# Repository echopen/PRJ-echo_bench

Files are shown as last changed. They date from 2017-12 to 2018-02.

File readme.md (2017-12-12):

Project
=======

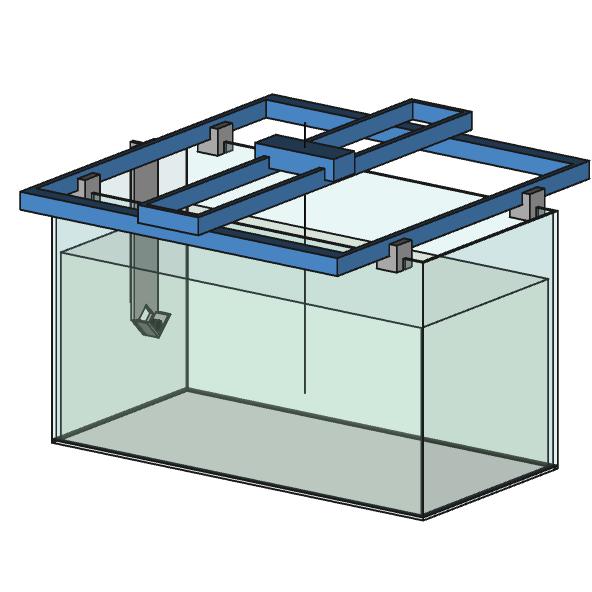
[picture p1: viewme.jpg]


Name
----

[2017-09-01 PRJ echo_bench]

Title
-----

Automatic ultrasonic transducers characterisation test bench

Description
-----------

This test bench is dedicated to the measurement of ultrasonic transducer
performances, such as:

-   experimental identification of the optical focus;

-   characterisation of the sound field in two dimensions (for example on a 5 x
    20cm plane);

-   influence of diverse parameters on the measurement quality (tension, length
    of impulse, settings of the analogical acquisition);

-   measurement of the variance of technical characteristics between different
    sensors of a same production batch;

-   geometrical validation/correction of an image captured by a complete probe.

Technical specifications and part list are available [here](../doc/2017-09-01
SPEC echo_bench_tranducer_test_bench en.pdf)

Ressources
----------

TODO

Installation
------------

TODO

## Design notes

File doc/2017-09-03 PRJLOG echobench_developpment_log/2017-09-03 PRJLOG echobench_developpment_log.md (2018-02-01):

# echOpen - Project log : EchoBench developpment

Daily log of the echOpen transducers test bench

| Objet :        | This document will show the project developpment progression with many photos and some comments. |
| -------------- | ---------------------------------------- |
| **Réf/File :** | `2017-09-03 PRJLOG echobench_developpment_log en` |
| **Révision :** | v1 - 2017-09-03 - BVi - Creation         |
| **Révision :** | work in progress                         |

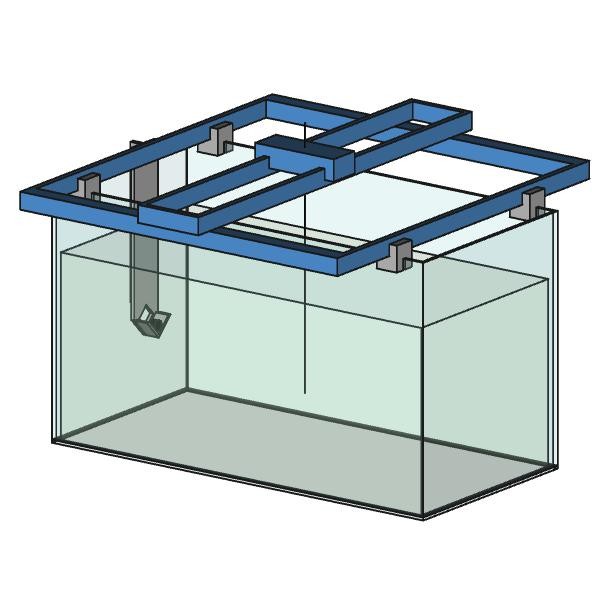
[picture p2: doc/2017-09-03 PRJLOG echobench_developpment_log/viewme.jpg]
viewme


## 2017-09-10 Assemblage Raspberry Pi Zero W & US-SPI

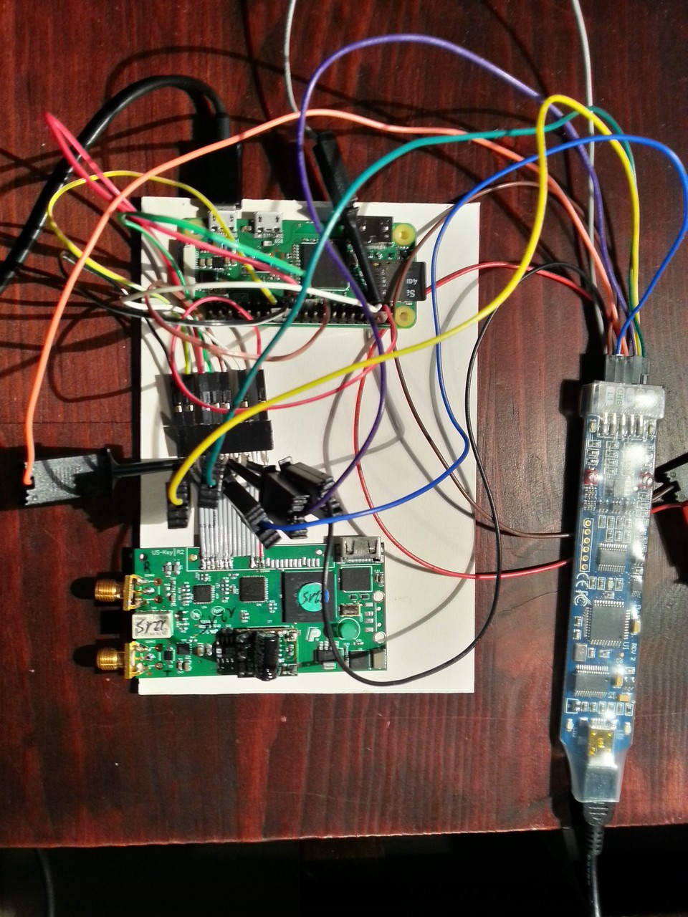
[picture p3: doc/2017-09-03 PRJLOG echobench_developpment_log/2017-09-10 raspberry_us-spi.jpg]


### Installation RPi zero W

#### Installation Raspbian

#### Config wifi en mode headless

D'après https://core-electronics.com.au/tutorials/raspberry-pi-zerow-headless-wifi-setup.html

Il suffit d'ajouter un fichier `wpa_supplicant.conf` à la carte SD de boot. Il sera "consommé" au prochain boot pour surcharger le fichier de configuration Wifi `/etc/wpa_supplicant/wpa_supplicant.conf`. Il doit contenir :

```
network={
    ssid="Your SSID"
    psk="YourWPAPassword"
    key_mgmt=WPA-PSK
}
```

Cette opération est à reproduire à chaque changement d'access point Wifi. On peut mettre plusieurs config :

```
network={
   ...
}

network={
   ...
}
```

#### Config mode "Ethernet Gadget"

D'après https://learn.adafruit.com/turning-your-raspberry-pi-zero-into-a-usb-gadget/ethernet-gadget

* Connexion SSH depuis windows
* On peut scanner et tester la connexion Wifi avec :
```
ifconfig
iwconfig wlan0
sudo iwlist wlan0 scan
```

#### Maj système :
```
sudo apt-get update
sudo apt-get upgrade
sudo rpi-update
sudo apt-get autoremove
```

#### Partage répertoire de travail avec Samba !!! ne fonctionne pas !!!

D'après http://www.framboise314.fr/partager-un-repertoire-sous-jessie-avec-samba/

* Installation serveur Samba
```
sudo apt-get install samba samba-common-bin
```

* Faites une copie de sauvegarde du fichier de configuration
```
sudo cp /etc/samba/smb.conf /etc/samba/smb.conf.org
```

* Editer le fichier `/etc/samba/smb.conf`
```
# The specific set of interfaces / networks to bind to
# This can be either the interface name or an IP address/netmask;
# interface names are normally preferred
interfaces = 127.0.0.0/8 eth0
bind interfaces only = yes
```

* Créez le dossier que vous souhaitez partager (s’il n’existe pas). J’ai choisi `/home/pi`.

* Maintenant rendez vous à la fin du fichier… oui, tout en bas et ajoutez :
```
[pihome]
comment = code folder
path = /home/pi
writeable = yes
browseable = yes
read only = no
guest ok = yes
guest only = yes
create mask = 0755 ????
create mode = 0777
directory mode = 0777
share modes = yes
```

* Définir le mot de passe réseau pour `pi`
```
sudo smbpasswd -a pi
```

* Redémarrez Samba sous (Jessie):
```
sudo systemctl restart smbd.service
```

#### Configuration Wifi
A défaut de pouvoir faire fonctionner SAMBA sur ethernet over USB on configure le wifi d'après https://core-electronics.com.au/tutorials/raspberry-pi-zerow-headless-wifi-setup.html :
* Sous SSH éditer le fichier `/boot/wpa_supplicant.conf` en y insérant (le choix est fait en dans l'ordre et en fonction des puissances :
```
network={
    ssid="Bivi's2-5G"
    psk="...password..."
    key_mgmt=WPA-PSK
}
network={
    ssid="Bivi's2"
    psk="...password..."
    key_mgmt=WPA-PSK
}
network={
    ssid="Bivi's"
    psk="...password..."
    key_mgmt=WPA-PSK
}
```

Avec cette config, en rebootant, la freebox attribue l'IP 192.168.1.120 au RPi et le partage pihome fonctionne correctement avec l'explorateur de fichier Windows sous \\192.168.1.120\pihome

#### Installation Python3 et lib

* Installer Pip3
```
sudo apt-get install python3-pip`
sudo python3 -m pip install --upgrade pip`
```

* Installer bottle, le serveur http et websocket pour Python3
```
sudo pip3 install bottle
sudo pip3 install python-dev !!! ECHEC !!!
sudo pip3 install gevent-websocket
```
* Tester bottle en exécutant les fichier `python3 bottle_hello.py` :
```python
from bottle import route, run, template

@route('/hello/<name>')
def index(name):
    return template('<b>Hello {{name}}</b>!', name=name)

run(host='0.0.0.0', port=8080)
```

* Installer l'accès au bus SPI
  D'après http://deusyss.developpez.com/tutoriels/RaspberryPi/PythonEtLeGpio/

* Lancer sudo raspi-config et valider le SPI dans Advanced options :
```
sudo raspi-config
```
* Après reboot, tester la présence du driver SPI :
```
lsmod | grep spi_
```
* Installation modules python pour SPI
```
sudo pip3 install spidev
```

## 2017-09-15 Montage Table XY

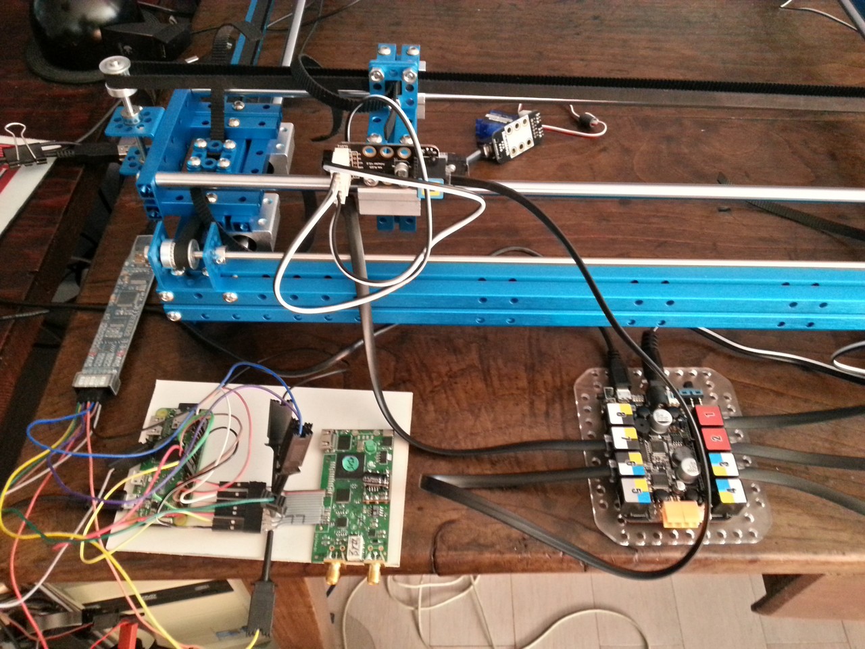
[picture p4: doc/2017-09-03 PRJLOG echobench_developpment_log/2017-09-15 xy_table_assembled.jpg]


## 2017-10-06 Premiers essais

Fantôme de pôche ;-)

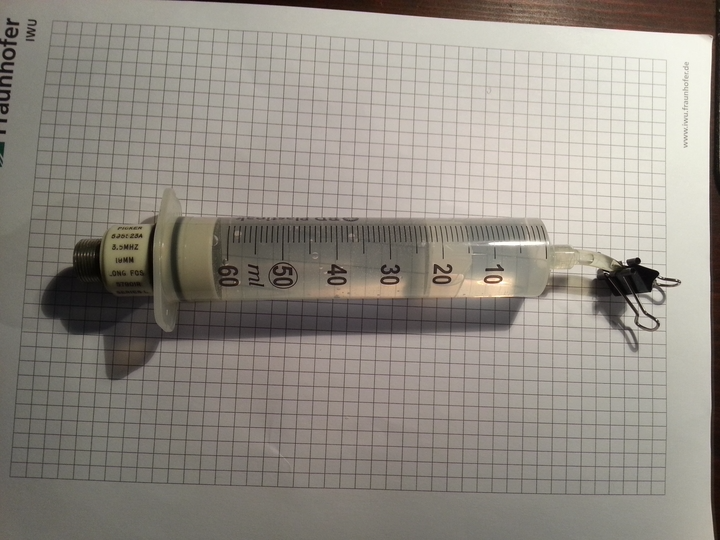
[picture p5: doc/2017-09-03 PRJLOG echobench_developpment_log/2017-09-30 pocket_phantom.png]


IHM sur navigateur Web

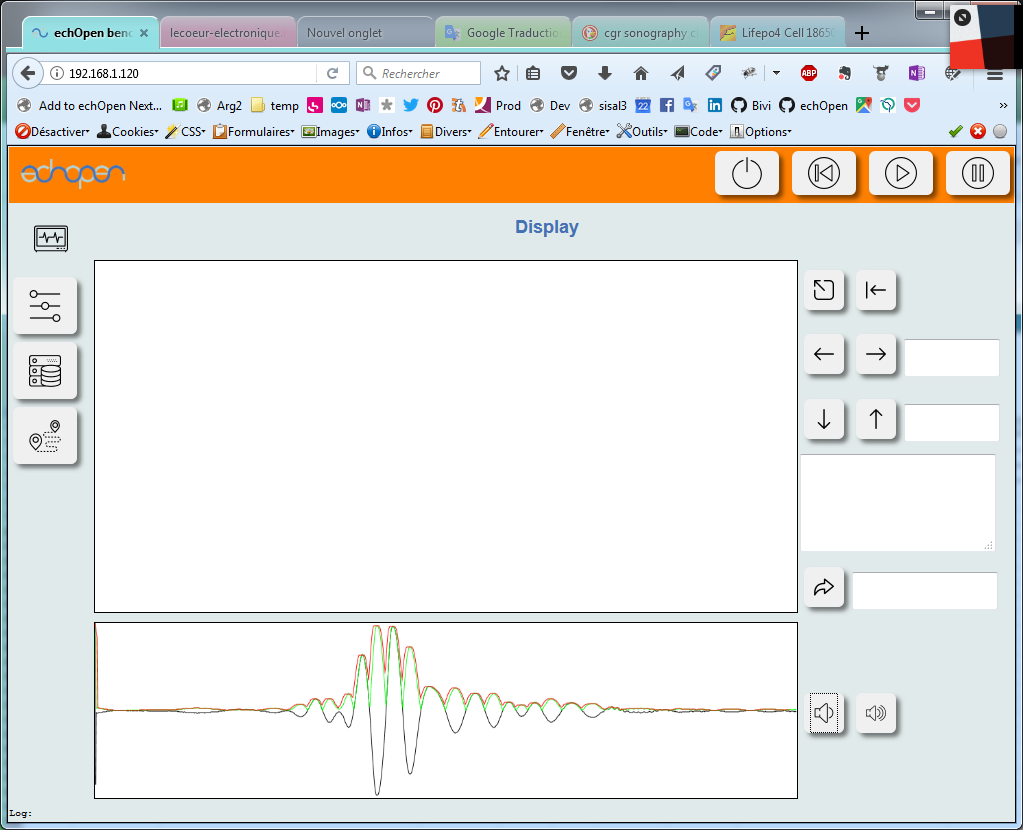
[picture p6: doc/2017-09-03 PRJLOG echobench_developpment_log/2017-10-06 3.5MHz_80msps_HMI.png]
2017-10-06 3.5MHz_80msps_HMI
Echantillonnage à 20Msps

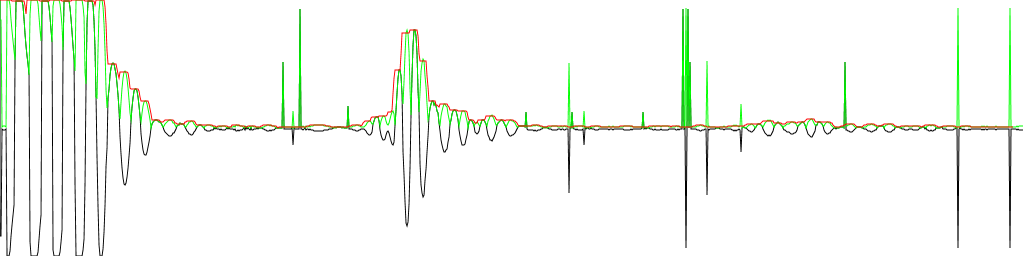
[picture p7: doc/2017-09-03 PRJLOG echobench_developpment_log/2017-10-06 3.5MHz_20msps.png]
2017-10-06 3.5MHz_20msps


Echantillonnage à 160Msps

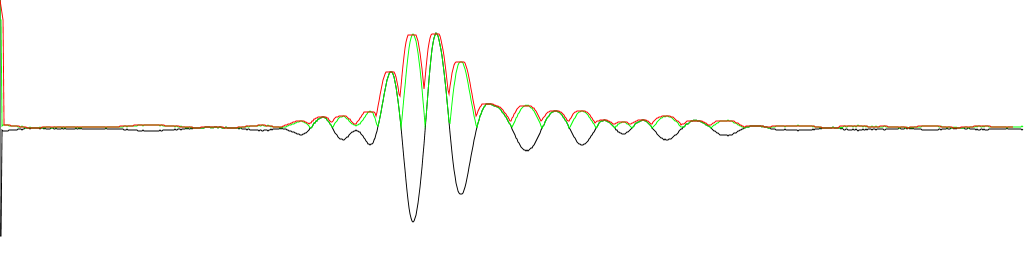
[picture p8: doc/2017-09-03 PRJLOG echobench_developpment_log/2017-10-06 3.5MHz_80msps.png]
2017-10-06 3.5MHz_80msps


## 2017-11-05 Adaptation Table XY sur aquarium (ou jardinière)

### Connexion Table XY <-> RPi0

On va établir une connexion série mais **attention** les niveau logiques sont à 3.3V côté RPi 
et 5V côté carte Me Orion (Arduino) de MakeBlock. Il faut un adaptateur de niveau :
* Le "Me Shield for Raspberry Pi" de chez MakeBlock http://learn.makeblock.com/en/me-shield-for-raspberry-pi/ (en stock chez Roboshop http://www.robotshop.com/en/makeblock-me-shield-raspberry-pi.html)
* Ou un adaptateur de niveau std https://hackspark.fr/fr/3-3v-5v-logic-level-converter.html ou https://hackspark.fr/fr/8-channel-bi-directional-logic-level-converter-txb0108-3-3-5v-or-others.html
* On évitera l'adaptation de niveau par pont diviseur qui présente un danger pour le T car la pin RX côté Arduino peut rester au niveau 5V dans certains cas.
  Un article complet sur la connexion Rpi Arduino : https://oscarliang.com/raspberry-pi-and-arduino-connected-serial-gpio/

### Pilotage de la table par le RPi

Au lieu d'utiliser les logiciels de dessin de haut niveau fournis avec la table (mDraw ou BenBox), nous allons installer sur la carte Me Orion de la table le firmware de pilotage CNC GCodeParser : https://github.com/Makeblock-official/XY-Plotter-2.0. Il interprète habituellement les commandes envoyées par le logiciel PC GRemote mais dans notre cas nous  enverrons directement les commandes depuis un script Python (serveur HTTP Bottle) via le port série.

### Codes G

```
G0  Xnnn Ynnn Znnn (Avance rapide)
G1  Xnnn Ynnn Znnn Fnnn (Avance usinage)
G2  Xnnn Ynnn Znnn Innn Jnnn (arc sens horaire)
G3  Xnnn Ynnn Znnn Innn Jnnn (arc sens anti-horaire)
G4  Pnnn (Pause)
G20 (Inch)
G21 (mm)
G28 (Home 0,0,0)
G30 Xnnn Ynnn Znnn (Home via XYZ)
G90 (Abs positionning)
G91 (Incr positionning)
G92 (Set as home)
$1  Xnnn Ynnn Znnn (set XYZ STEP PIN)
$2  Xnnn Ynnn Znnn (set XYZ DIR PIN)
$3  Xnnn Ynnn Znnn (set XYZ Min PIN)
$4  Xnnn Ynnn Znnn (set XYZ Max PIN)
$5  Znnn (ENABLE SERVO MOTOR FOR Z)
$6  Xnnn Ynnn Znnn (set XYZ STEPS PER MM)
$7  Xnnn Ynnn Znnn (set XYZ fast FEEDRATE)
$8  Snnn (set XYZ INVERT LIMIT SWITCH)
```

### Usage NetBeans

Pour permettre à Netbeans d'ouvrir des projets quelconques (juste une arborescence de fichier, sans fichier projet)
* Installer le plugin "Automatic Projects"

### Install Makeblock Library for Arduino

D'après http://learn.makeblock.com/en/learning-arduino-programming/

### Liaison Série RPi0 <-> Arduino

D'après http://learn.makeblock.com/me-shield-for-raspberry-pi/
D'après https://electrosome.com/uart-raspberry-pi-python/

* Libérer /dev/ttyAMA0 en désactivant le Bluetooth (cf https://www.raspberrypi.org/documentation/configuration/uart.md, https://hallard.me/enable-serial-port-on-raspberry-pi/). Depuis que les RPi sont équipés de Bluetooth (RPi3 et RPi0 W), l'UART hard est directement connecté au BT et un UART soft /dev/ttyS0 est connecté au GPIO 14 et 15. Il faut ici le récupérer
```
sudo nano /boot/config.txt
... ajouter à la fin la ligne:
dtoverlay=pi3-disable-bt
... sauver/quiter
sudo systemctl disable hciuart
... rebooter
sudo shutdown -r now
```
* Installer pyserial
```
sudo apt-get install python-serial
sudo pip3 install pyserial
```
* Reboucler RX/TX et tester :
```
python -m serial.tools.miniterm /dev/ttyAMA0 115200
... ou
minicom -b 115200 -o -D /dev/ttyAMA0
```

### Pieds supports

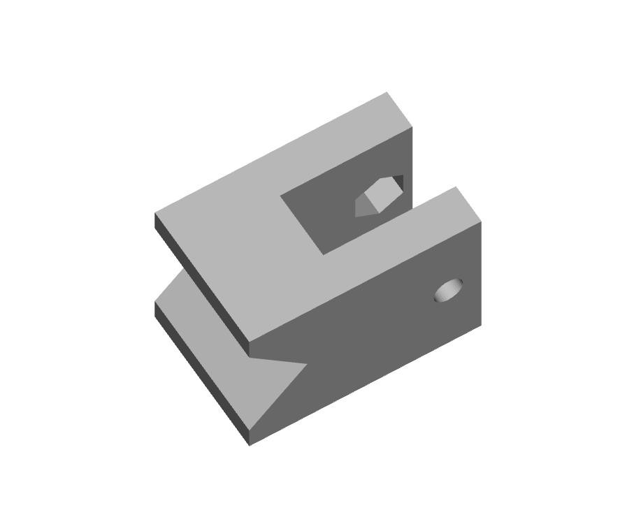
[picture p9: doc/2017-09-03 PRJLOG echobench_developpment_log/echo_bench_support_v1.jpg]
echo_bench_support_v1


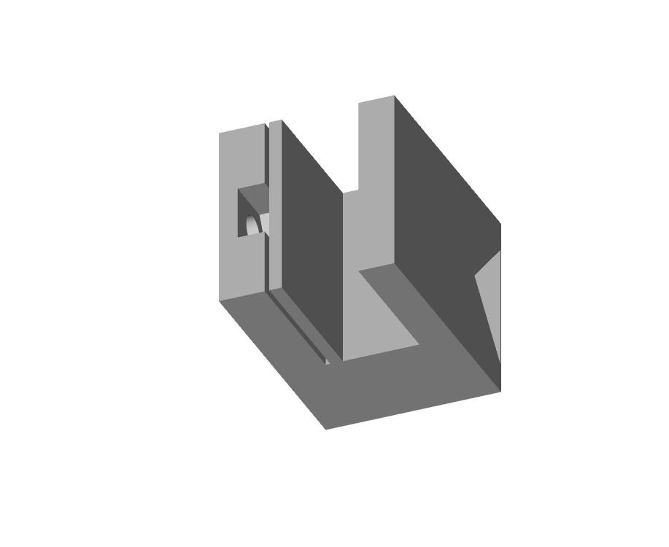
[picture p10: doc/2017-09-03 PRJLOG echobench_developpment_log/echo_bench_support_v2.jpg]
echo_bench_support_v1


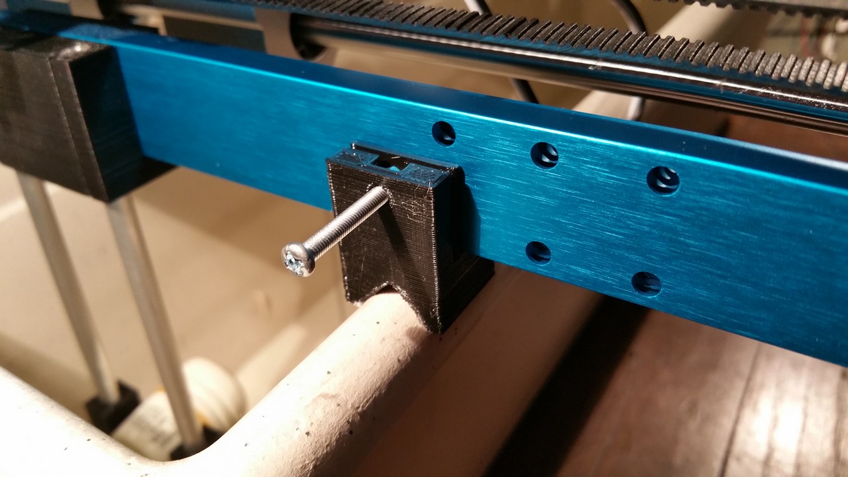
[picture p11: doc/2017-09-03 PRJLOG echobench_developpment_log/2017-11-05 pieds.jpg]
2017-11-05 pieds


### Support de transducteur

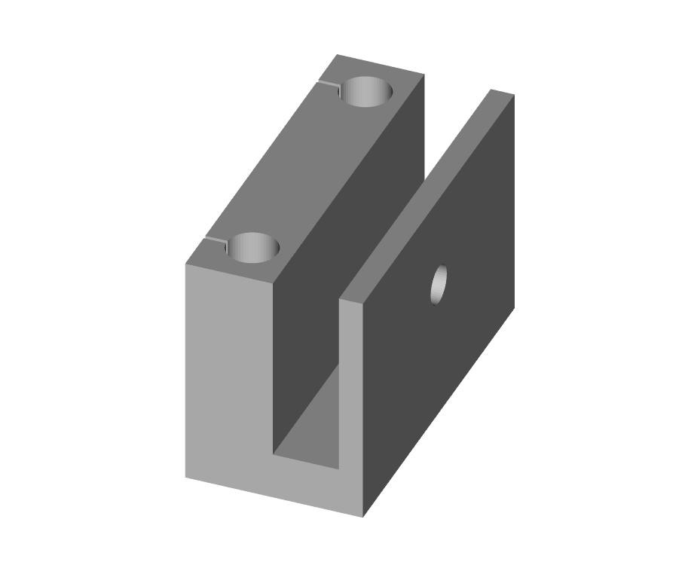
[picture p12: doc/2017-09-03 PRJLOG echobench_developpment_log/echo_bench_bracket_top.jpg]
echo_bench_bracket_top


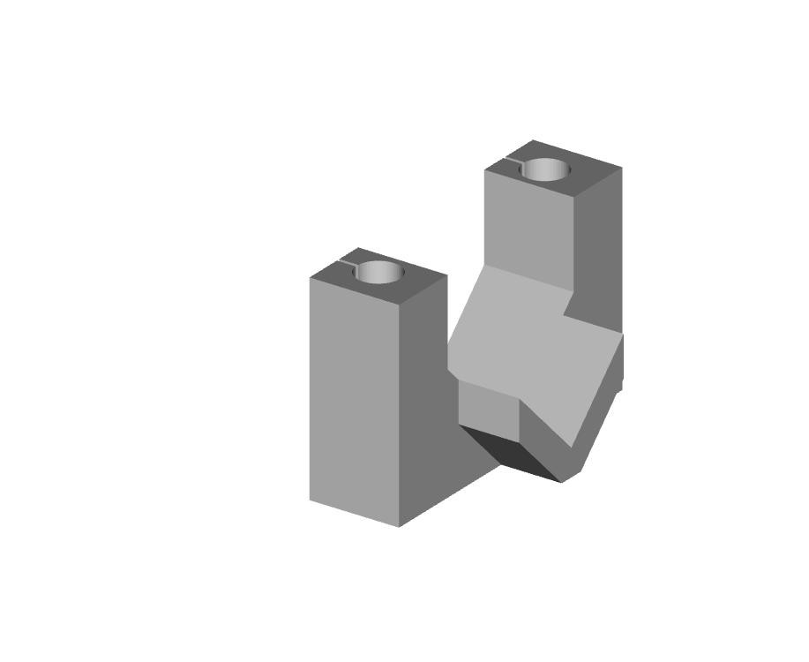
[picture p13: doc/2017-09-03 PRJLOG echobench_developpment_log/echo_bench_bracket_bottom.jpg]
echo_bench_bracket_bottom


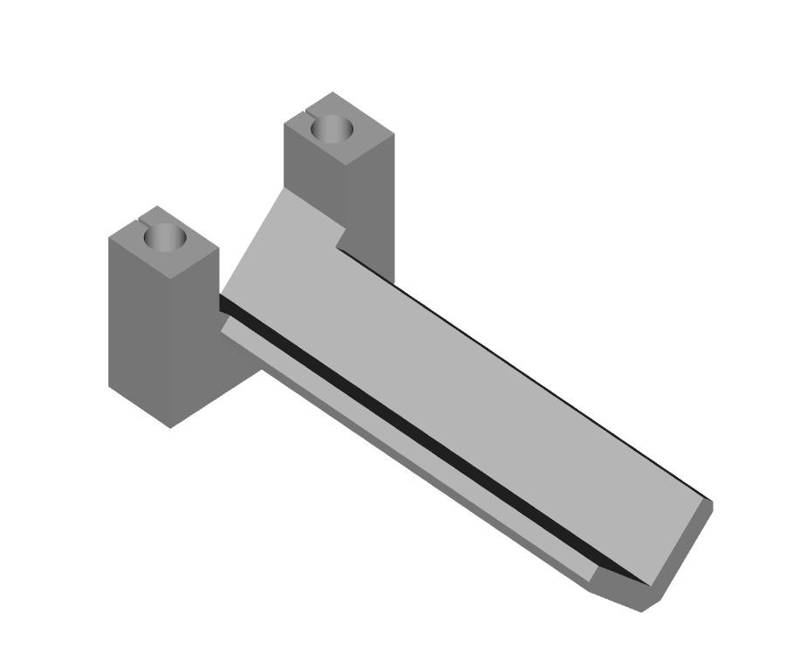
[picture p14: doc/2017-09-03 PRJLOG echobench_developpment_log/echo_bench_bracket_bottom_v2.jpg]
echo_bench_bracket_bottom_v2


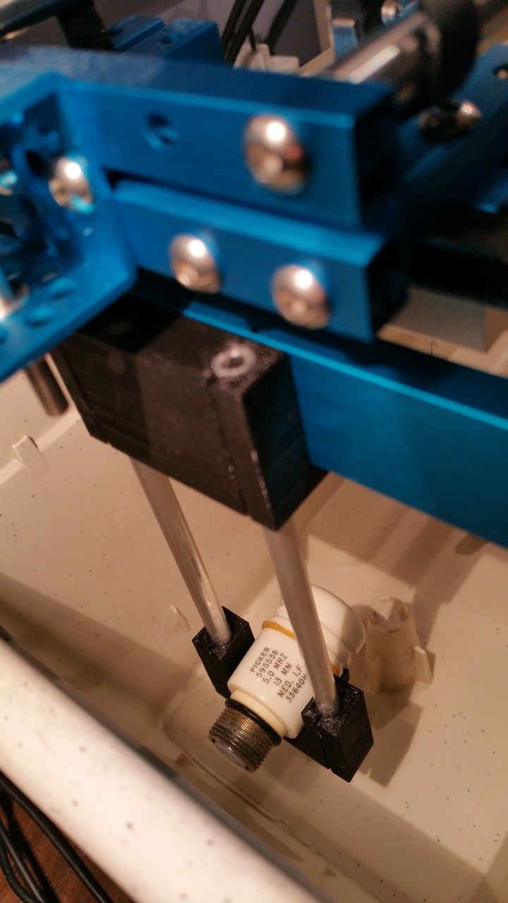
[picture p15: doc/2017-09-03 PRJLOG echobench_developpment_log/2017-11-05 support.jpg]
2017-11-05 support


### Pince de cible métallique

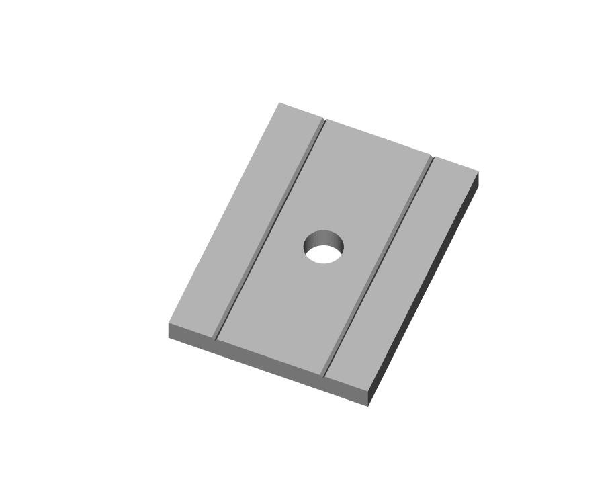
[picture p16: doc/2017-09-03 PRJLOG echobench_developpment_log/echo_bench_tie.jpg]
echo_bench_tie


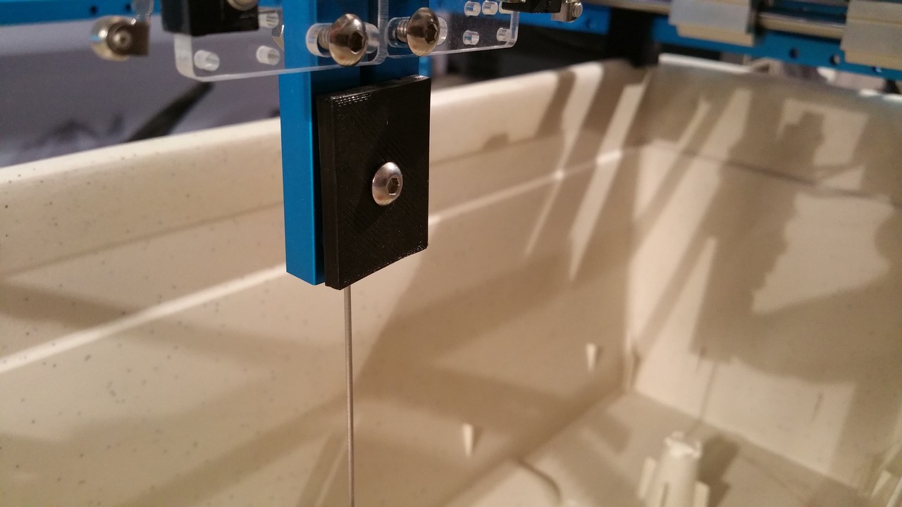
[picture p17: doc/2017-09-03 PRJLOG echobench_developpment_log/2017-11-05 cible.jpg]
2017-11-05 cible


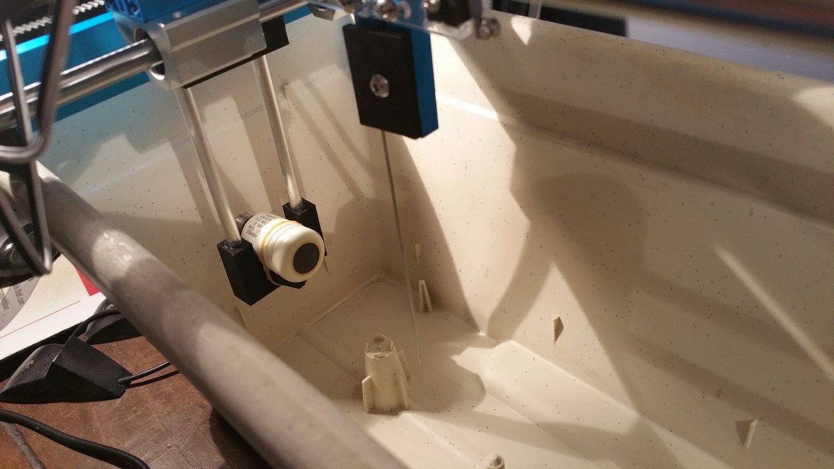
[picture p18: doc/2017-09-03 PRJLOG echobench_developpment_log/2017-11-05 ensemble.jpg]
2017-11-05 ensemble


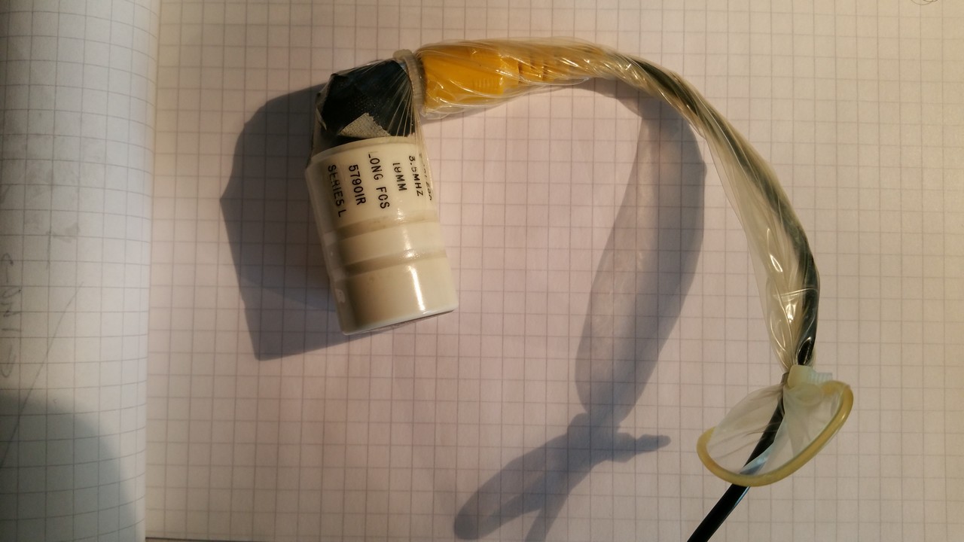
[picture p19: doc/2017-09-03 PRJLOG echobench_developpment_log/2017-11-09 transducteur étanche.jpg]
2017-11-09 transducteur étanche


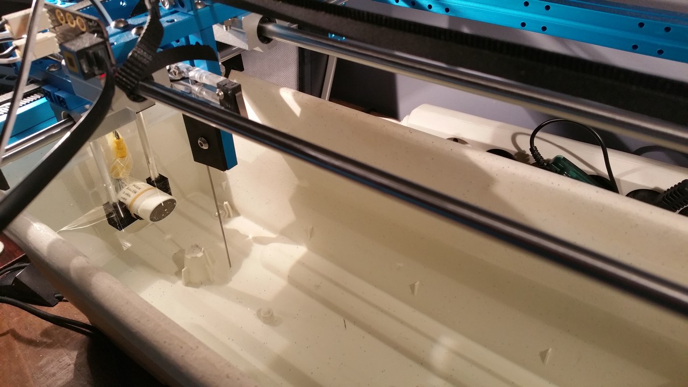
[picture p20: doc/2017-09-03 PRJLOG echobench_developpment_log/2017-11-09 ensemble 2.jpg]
2017-11-09 ensemble 2
Premier essai

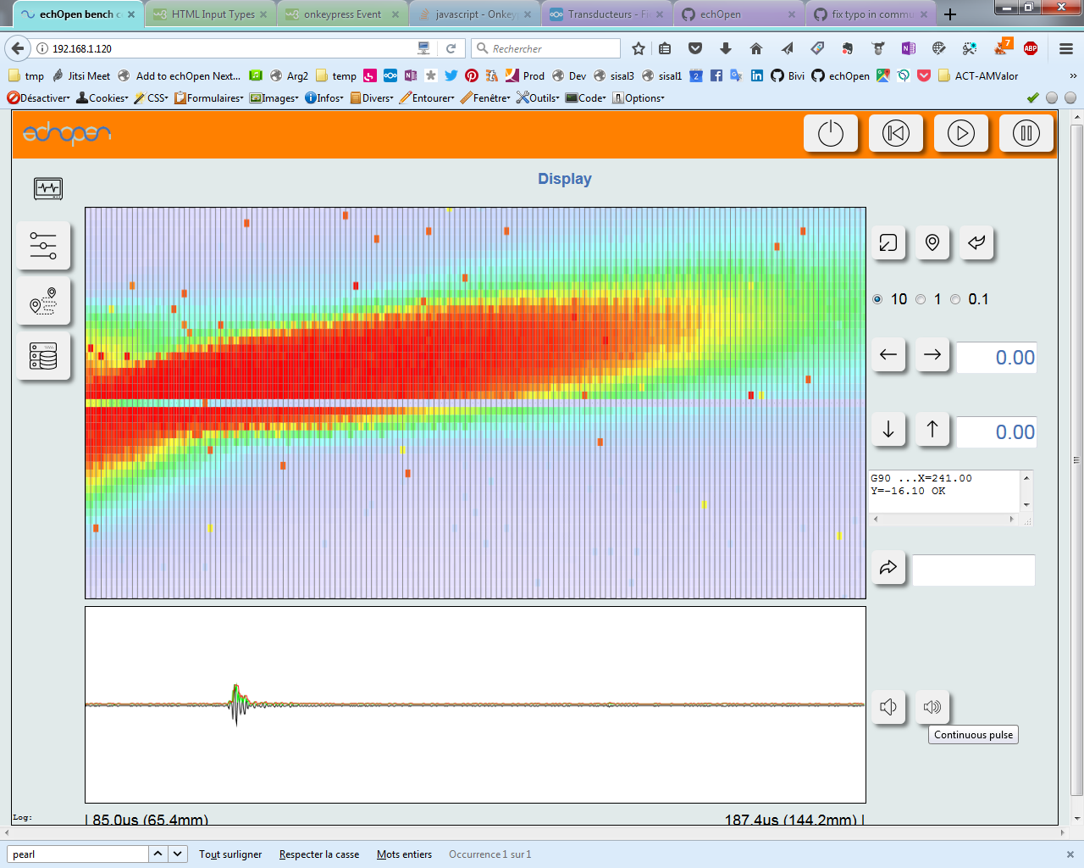
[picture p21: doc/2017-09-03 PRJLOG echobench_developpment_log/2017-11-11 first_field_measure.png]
2017-11-11 first_field_measure


## 2017-11-16 Essais tranducteur en direct

Echelle orthonormée.

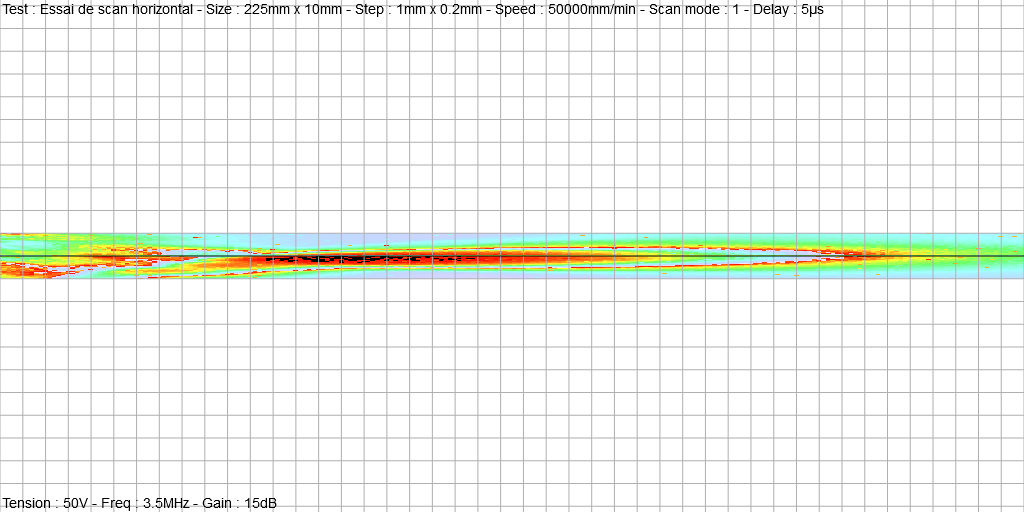
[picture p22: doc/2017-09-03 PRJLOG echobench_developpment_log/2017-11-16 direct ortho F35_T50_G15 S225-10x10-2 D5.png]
2017-11-16 direct ortho F35_T50_G15 S225-10x10-2 D5


Echelle dilatée en Y.

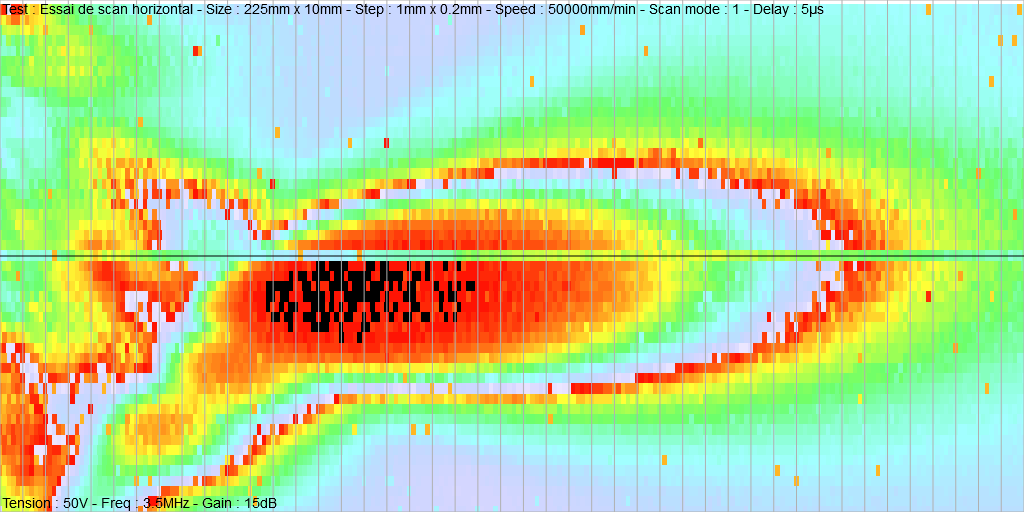
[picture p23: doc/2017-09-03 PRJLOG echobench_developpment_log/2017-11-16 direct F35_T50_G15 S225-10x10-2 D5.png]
2017-11-16 direct F35_T50_G15 S225-10x10-2 D5


## 2017-11-16 Essais avec périscope

Essai avec un périscope, mais miroirs de mauvaise qualité.

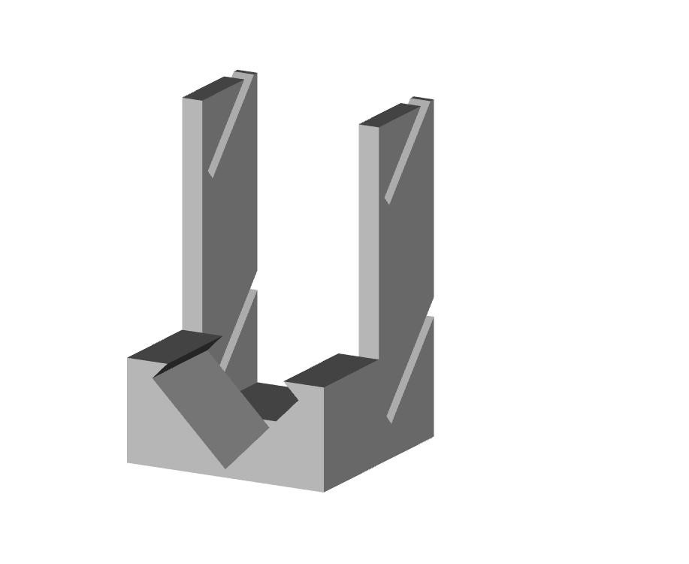
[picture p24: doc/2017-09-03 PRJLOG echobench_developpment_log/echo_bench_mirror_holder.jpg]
echo_bench_mirror_holder


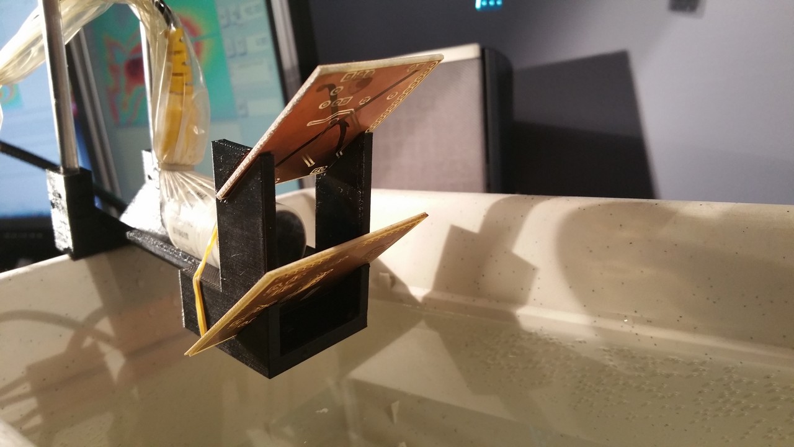
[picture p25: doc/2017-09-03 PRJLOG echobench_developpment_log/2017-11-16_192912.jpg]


2017-11-16c periscop F35_T65_G20_S225-10x10-2_D90 miroirs

## 2017-11-18 Essais avec un miroir à 45°

Support miroir à 45°. Le miroir est un bout de PCB simple face de 45x30.

echo_bench_single_mirror_holder



2017-11-18 mirror_inclined_target F35_T75_G16_S225-10x10-2_D40

## 2017-11-19 Réglage verticalité de la tige cible

Réglagle de l'angle de la tige cible par rapport à la verticale pour maximiser l'echo à 150mm.



Le résultat obtenu est meilleur et comparable à la mesure sans miroir à tension et gain identiques.



## 2017-11-19 Mesures affichées en dB

2017-11-19 mirror dB F35_T50_G15_S225-10x10-2_D35

## 2017-11-26 Ajout Lib plotly et mesure imasonic

2017-11-27 35labo

2017-11-27 35labo

2017-11-27 35labo

## 2017-11-24 Cible avec fil de nylon
echo_bench_bow

2017-11-24_archet

2017-11-24_archet2

## 2018-01-31 Connexion console par Bluetooth

D'après https://hacks.mozilla.org/2017/02/headless-raspberry-pi-configuration-over-bluetooth/
et https://github.com/DrRowland/RPi-Bluetooth-Console/blob/master/setup.sh

```
sudo apt-get update
sudo apt-get upgrade
sudo apt-get install bluetooth bluez blueman
```

----
----
----
----
----
----
----
# Poubelle !!!

### Communication RPi / PyBoard

* Installer PySerial : 
  `python -m pip install pyserial`
* Installer le serveur Web Bottle et l'extension pour faire du WebSocket :
  `pip install bottle`  
  `pip install python-dev`
  `pip install gevent-websocket`

## Installation RPi

#### Mise à jour du système

~~~~sh
sudo apt-get update
sudo apt-get upgrade
sudo rpi-update
sudo apt-get autoremove
~~~~
=> avec rpi-update le firmware passe de   Linux raspberrypi 4.1.19-v7+ #858  à   rpi-4.4.y

Et reboot ! ... perte écran LCD :-(

### Config Samba

### Reconfiguration écran LCD

Atteindre le wiki Waveshare http://www.waveshare.com/wiki/3.5inch_RPi_LCD_\(A\) et télécharger la dernière version des drivers : http://www.waveshare.com/w/upload/3/3d/LCD-show-160811.tar.gz

Extraire l'archive dans `/home/pi/LCD-show` et :

~~~~sh
cd LCD-show
./LCD35-show
~~~~
  ```

  ```

```

```

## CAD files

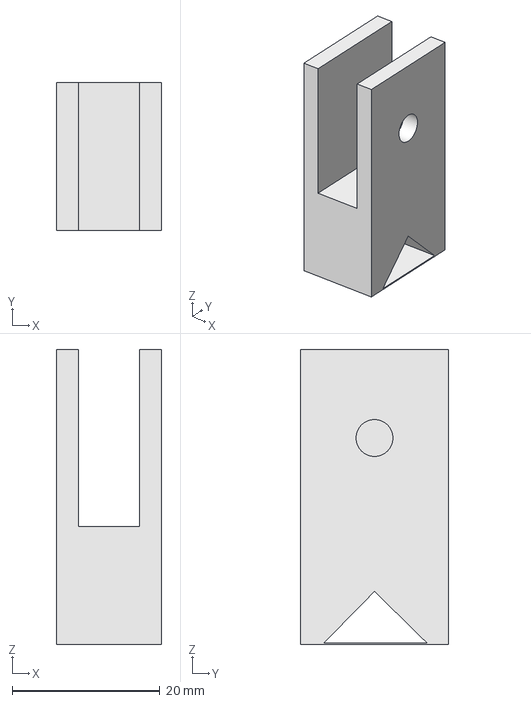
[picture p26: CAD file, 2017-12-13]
cad/echo_bench_foot_v3_fcv16.FCStd
14.3 x 20.0 x 40.0 mm

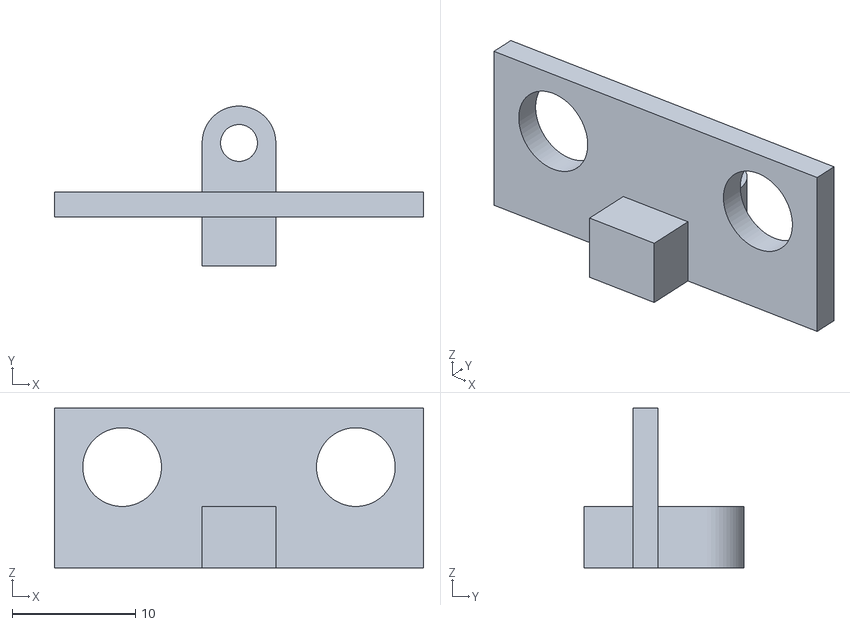
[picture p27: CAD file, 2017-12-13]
cad/echo_bench_pcb_frame_flange.stl
30.0 x 13.0 x 13.0

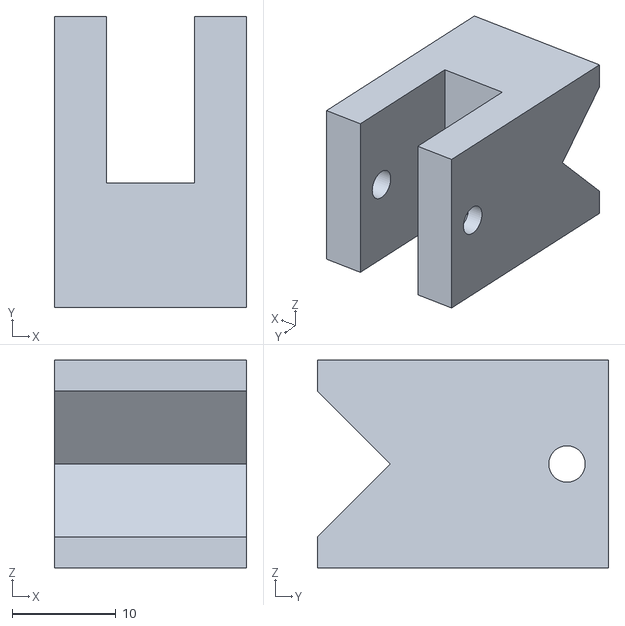
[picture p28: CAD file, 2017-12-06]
cad/echo_bench_support_v1.stl
18.5 x 28.0 x 20.0

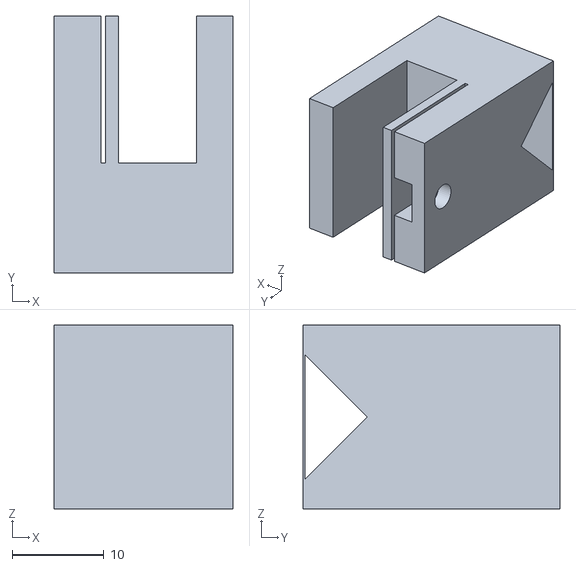
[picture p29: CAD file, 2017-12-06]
cad/echo_bench_support_v2.stl
19.5 x 28.0 x 20.0

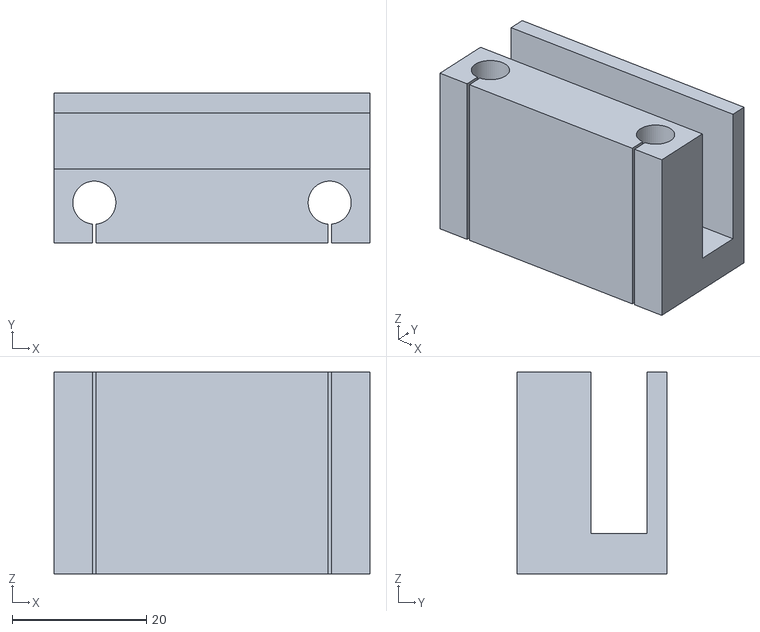
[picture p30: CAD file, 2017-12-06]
cad/echo_bench_bracket_top.stl
47.0 x 22.3 x 30.0

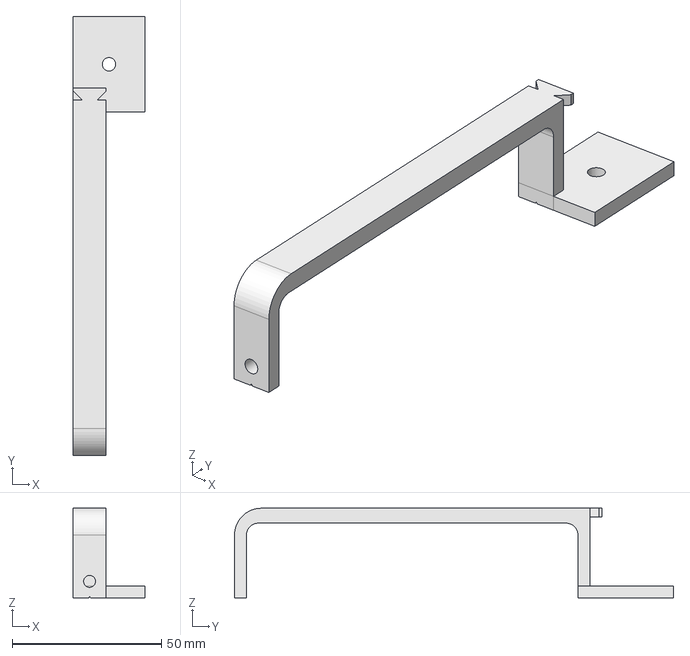
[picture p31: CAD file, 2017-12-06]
cad/echo_bench_bow_fcv16.FCStd
24.0 x 147.0 x 30.0 mm

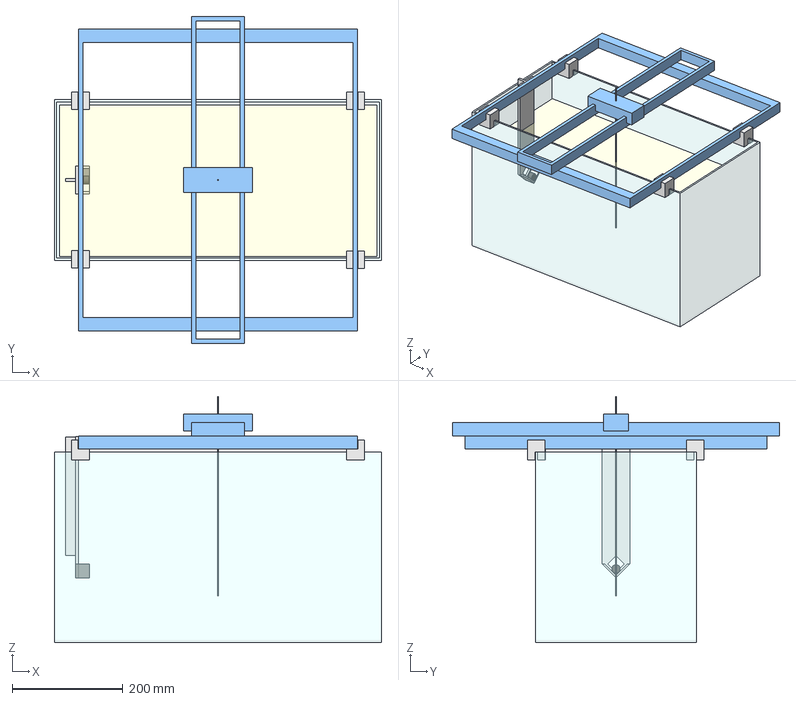
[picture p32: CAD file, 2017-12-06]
cad/echo_bench_view_fcv17.FCStd
590.0 x 590.0 x 444.0 mm

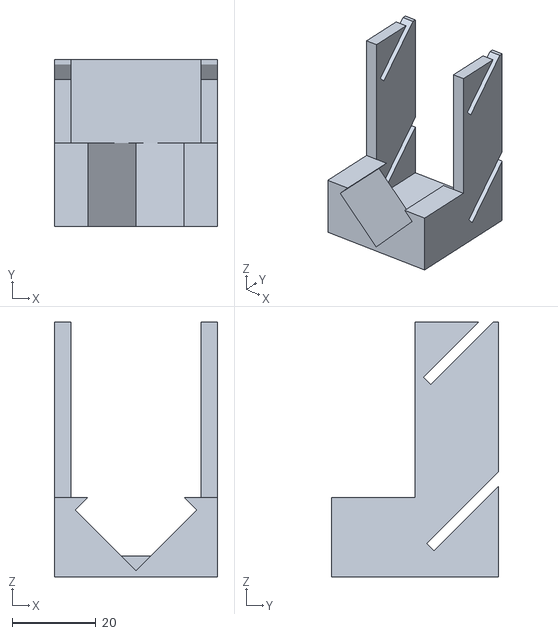
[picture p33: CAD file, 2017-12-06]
cad/echo_bench_mirror_holder.stl
39.0 x 40.0 x 61.0

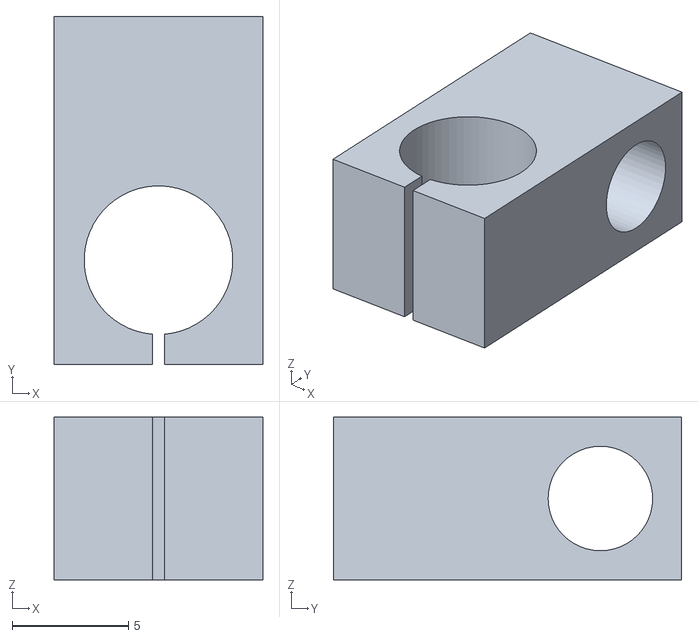
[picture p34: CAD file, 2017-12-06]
cad/test.stl
9.00 x 15.0 x 7.00

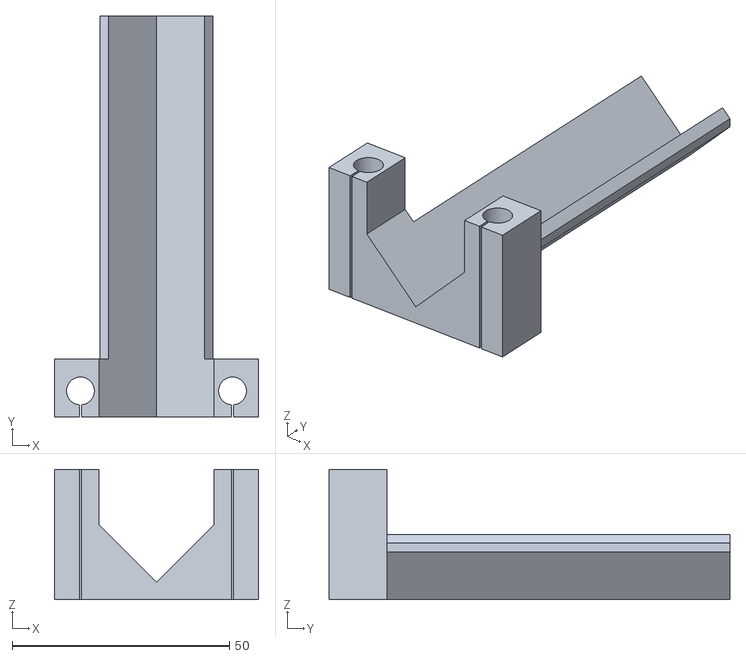
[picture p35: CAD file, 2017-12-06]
cad/echo_bench_bracket_bottom_v2.stl
47.0 x 92.3 x 30.0

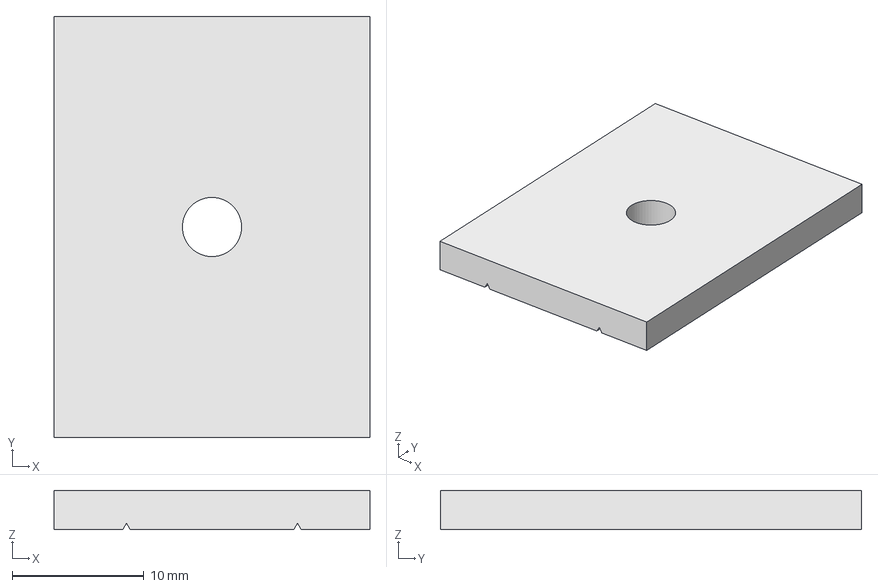
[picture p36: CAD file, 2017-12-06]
cad/echo_bench_target_tie.FCStd
24.0 x 32.0 x 3.00 mm

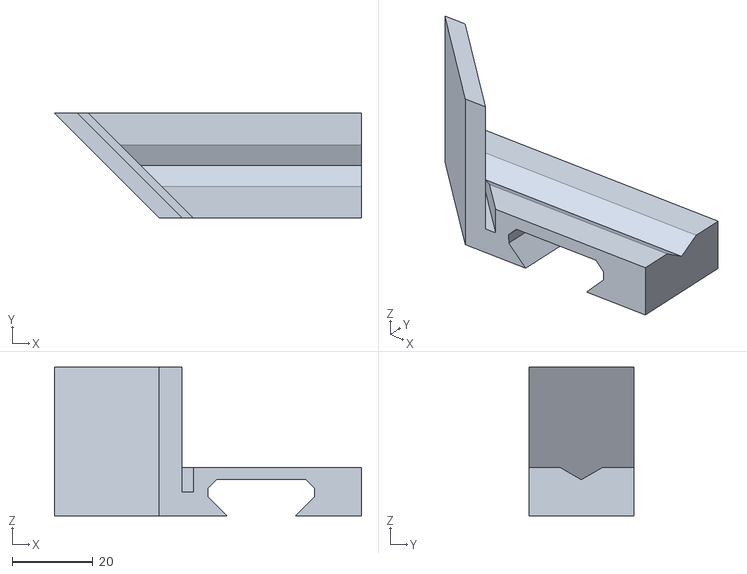
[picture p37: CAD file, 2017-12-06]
cad/echo_bench_single_mirror_holder.stl
76.3 x 26.0 x 37.0

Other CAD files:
cad/echo_bench_foot_v3.stl
cad/echo_bench_pcb_frame_fcv17.FCStd
cad/echo_bench_foot_v1_fcv17.FCStd
cad/echo_bench_bow.stl
cad/echo_bench_foot_v2_fcv17.FCStd
cad/echo_bench_tie.stl
cad/echo_bench_bracket_bottom.stl
cad/echo_bench_bracket_fcv17.FCStd
cad/echo_bench_pcb_frame_washer.stl

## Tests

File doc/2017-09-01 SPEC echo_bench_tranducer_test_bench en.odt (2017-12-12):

Objet : | Specifications of a test bench for the automatic characterization of ultrasonic transducers
Reference/File: | 2017-09-01 SPEC echo_bench_transducer_test_bench en
Revision: | v1 | 2017-09-01 | BVi | Created
Revision: | v2 | 2017-12-01 | BVi | Template update
Revision: | In progress | 2017-12-04 | JBo | Translation FR->EN

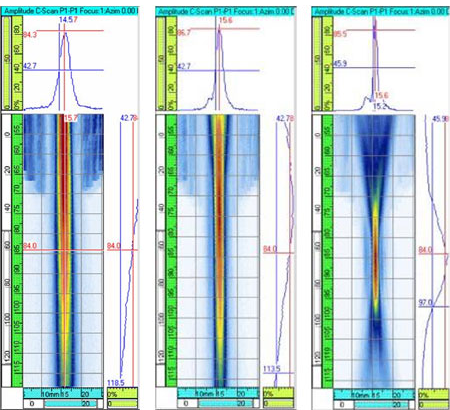
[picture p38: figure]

The test bench should allow precise and reproducible measurement of ultrasonic transducer performances:

- experimental identification of the optical focus;
- characterization of the sound field in two dimensions (for example on a 5 x 20cm plane);
- influence of diverse parameters on the measurement quality (tension, length of impulse, settings of the analogical acquisition);
- measurement of the variance of technical characteristics between different sensors of a same production batch;
- geometrical validation/correction of an image captured by a complete probe.

Knowing precisely the focus field of a transducer will allow the programming of corrective numerical end-of-pipe image processing algorithms (such as refocusing processes, for example provided here http://refocus-it.sourceforge.net/ and here http://www.focusmagic.com/)

# Off-the-shelf components

Component | Sourcing | License
XY Plotter Robot from MakeBlock with Arduino controller | Purchased, 321€ incl. VAT, see for example here https://www.lextronic.fr/P30523-table-traante-plotter-xy-v20.html | Partly open source and proprietary
Signal acquisition card US-SPI | US-SPI, Lecoeur Electronique (http://www.lecoeur-electronique.net/crbst_16.html) | Proprietary
Raspberry Pi (ZERO or v3) | https://www.raspberrypi.org/products/raspberry-pi-zero-w/ | Proprietary
MMI Device | Any computer with a standard browser | N/A

# Custom parts

Part | Sourcing
Aquarium feet | 3D printed
Universal transducer support | 3D printed
Target support | 3D printed
Electronic support | 3D printed

# Communications

Here is an overview of exchanges between the different subsystems:

- Transducer ↔ US-SPI (low amplitude analogic signals)
  - US-SPI provides a -100V pulse
  - Transducer returns an analogic signal
- US-SPI ↔ Raspberry Pi (binary commands on US-SPI, 5V, 8MHz)
  - Raspberry Pi provides pulse configuration and measurement order
  - US-SPI provides the measured raw data at 80Msps (mega samples per second) max.
- XY Robot ↔ Arduino controller (power electronics)
  - XY Robot provides sensed information such as axis position or limit switch
  - Arduino controller provides function signal to the motors and accessories
- Raspberry Pi ↔ Arduino controller (ISO ASCII commands on USB, UART or SPI)
  - Raspberry Pi provides translation commands on axes XY (ISO code)
  - Arduino XY table confirms when required position is reached.
- Raspberry Pi ↔ MMI (HTTP on Ethernet, WiFi or Ethernet over USB)
  - The MMI (web browser) allows setting measurement parameters (pulse settings, acquisition settings, surface to explore, etc.), manual control of the XY Robot and US-SPI (translation, test pulse, etc.)
  - Raspberry Pi provides the HTTP server with user interface pages and returns data files

# Software

Following software development is required:

- HTTP server on Raspberry Pi programed with python (eventually with bottle (https://bottlepy.org/docs/dev/)) and providing
  - Communication with US-SPI
  - Communication with the Arduino controller. Caution: the controller is designed to communicate via USB with a Windows PC rather than with a Raspberry Pi. In case this does not work, it will always be possible to control the XY Robot with the Rasberry Pi.
  - Display a measurement progression bar
  - Collect measurement files (referencing measurement conditions and sensor identifier)
- A graphical application for the visualization of the performed measurements with a basic database of measurement files (a simple in-browser graphic display would be nice). This application should allow exporting a directory per sensor.

Why a HTTP server? The long-term objective is to run the browser on a Raspbery Pi (v3 would be required in this case) connected to its own keyboard and monitor. That way, the test bench could be completely autonomous. This is an advantage because the measurement campaigns may be long and therefore immobilize material resources. It would be then possible to connect to the test bench through the network (local or internet [tricky?]).

# Development and set up tasks

Task | Rough estimation of the required workload (in days)
Purchase | 1
Assembly of the XY Robot and initial set up | 2
3D printing of the aquarium feet, universal transducer support and target support | 2
Installation and configuration of the Raspberry | 2
Development of the communication library for the Raspberry Pi and XY Robot | 2
Development of the communication library for the Raspberry Pi and US-SPI | 2
Development of the HTTP server in python | 5
Data display | 4
Total | 20

# Use cases

The test bench can be used to:

- Validate target design (e.g. material and shape);
- Characterize a reference transducer (e.g. Imasonic);
- Characterize purchased transducers;
- Validate samples for the flooding material (oils or other materials);
- Measure the perturbations introduced by acoustic mirrors;
- Perform calibration measurements to be used in numerical correction.

# Transducer qualification protocol

<<This part of the documentation is still in progress>>

1. Capture a photo of the transducer on 5mm x 5mm graph paper
2. Write down the transducer references: manufacturer, product name, frequency, diameter, focus angle, focus length, dimensions of the focal zone at -6dB.
3. Sentence to be translated
4. Move the target to the focal point, where there is maxima echo and X. Set the verticality of the target. Set the horizontal angle by applying mechanical stress on the support tubes.
5. Sentence to be translated.
6. Set gain to 20dB and voltage to 70V. Set gMax just below the saturation level and raise voltage to let the curve touch the line 253. Write down the pair (gain, voltage).
7. At 160Msps, capture an image of the echo (in png and json) for the following settings
  a. Focal point, gMax. Save the result under “0dB.png/json”
  b. Focal point, 60dB, target moved to -10mm on the Y axis. Save the result under “noise_-10mm_60dB.png/json”
  c. Focal point, 60dB, target moved to -20mm on the Y axis. Save the result under “noise_-20mm_60dB.png/json”
  d. -6dB, x max, gMax. Save the result under “-6dB_x_max.png/json”
  e. -6dB, x min, gMax. Save the result under “-6dB_x_min.png/json”
  f. Zero, ?dB (for the pulse <255). Save the result under “pulse.png/json”
8. Go back to contact and Y=0. Sentence to be translated.
9. Look for the delay which allows displaying the echo (generally within the 5-15µs range).
10. Make a capture on 15x250 at 0.2x1mm with longitudinal sweeping.
11. Save the captured image.
12. Fill the measurement form to be archived with all the captured files.

# Remaining improvements for this document

- Sequence diagram displaying communications between subsystems
- Set a parameter list for measurements (breadth, length, X delay, Y delay, etc.)
- Measurement types: single firing, exploration with fixed or progressive grid, smart exploration (looking for characteristic points)
- Define the characterization procedure of a transducer and the corresponding deliverable.

Specifications : echoBench Transducer test bench

Specification : echoBench [2017-09-01 SPEC echo_bench_tranducer_test_bench en] v3 5/5

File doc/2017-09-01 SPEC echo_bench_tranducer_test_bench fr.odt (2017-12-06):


L’objectif du banc est de pouvoir réaliser des mesures précises et répétables sur les différents transducteurs que nous utiliserons :

- Détermination expérimentale du point de focalisation.
- Champ de focalisation en 2D (ex : dans un plan de 5cm x 20 cm).
- Influence des différents paramètres sur le qualité de la mesure (tension ou durée d’impulsion, réglage de la partie analogique de la chaîne d’acquisition…).
- Mesure de la dispersion des caractéristiques dans une série de capteurs d’un même lot.
- Validation/correction géométrique de l’image obtenue par une sonde complète.

Par ailleurs, la connaissance précise du champ de focalisation d’un transducteur pourra peut-être alimenter des algorithmes numériques d’amélioration d’image en fin de chaîne de traitement, à la manière de certains traitements d’image floues (http://refocus-it.sourceforge.net/, http://www.focusmagic.com/)

# Liste du matériel

1. Table XY MakeBlock avec électronique de commande 321€ TTC (https://www.lextronic.fr/P30523-table-traante-plotter-xy-v20.html).
2. Pieds pour aquarium (impression 3D)
3. Support transducteur universel (impression 3D)
4. Carte d’acquisition US-SPI
5. Raspberry Pi (ZERO ou v3)

# Communications

US-SPI Controleur XY Arduino Raspberry -100v Stepper SPI USB UART SPI TCP-IP HTTP Data

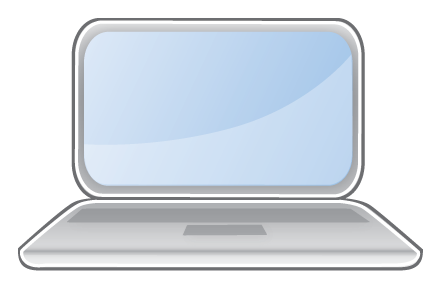
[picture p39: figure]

Les différents échanges entre les modules sont les suivants :

- Transducteur ↔ US-SPI (analogique faible signaux)
  - US-SPI → pulse -100V
  - Transducteur → signal analogique en retour
- US-SPI ↔ Rpi (commandes binaires sur SPI, 5V, 8MHz)
  - Rpi → configuration du tir, ordre de faire une mesure
  - US-SPI → données brutes de la mesure à 80 Msps maxi
- Table XY ↔ Contrôleur Arduino (analogique de puissance)
  - Table XY → informations telles que butées de fin de course
  - Contrôleur → ordres aux moteurs et accessoires
- Rpi ↔ Contrôleur Arduino (commandes ISO ASCII sur USB ou UART ou SPI)
  - Rpi → consignes de déplacement en XY (code ISO)
  - Table XY → acquittement position atteinte
- Rpi ↔ Interface de contrôle (HTTP sur Ethernet ou Wifi ou Ethernet_over_USB)
  - Interface de contrôle (navigateur WEB) → configuration de la mesure (caractéristique du tir, config acquisition, surface à explorer…), contrôle manuel table et us-spi (déplacement, tir d’essai...)
  - Rpi → serveur HTTP des pages d’interface utilisateur, retour fichiers data.

# Software

Le développement logiciel consistera en :

- Développer pour le Raspberry d’un serveur HTTP simpliste sous Python (« bottle »?) qui prendra en charge :
  - la communication avec l’US-SPI
  - la communication avec le contrôleur. /!\ le contrôleur est plutôt prévu pour communiquer via USB avec un PC sous Windows qu’avec un Rpi. En cas de « gros » pb on pourra toujours piloter directement les moteurs avec le Rpi.
  - Afficher un indicateur de progression d’une mesure
  - La collecte des fichiers de mesure (avec référence capteur et conditions de mesure)
- Une application de représentation graphique des mesures avec suivi rudimentaire des fichiers de mesure (un affichage simple en SVG sur navigateur serait un plus). Elle devra permettre d’exporter un « dossier » lisible par capteur

Pourquoi un serveur HTTP ? Parce que, à terme, on pourrait faire tourner aussi le navigateur sur le Raspberry (un Pi3 dans ce cas) équipé de son propre écran/clavier et rendre le banc de mesure complètement autonome car les mesures risquent d’immobiliser longtemps le matériel. On pourra aussi se connecter sur le banc à distance via le réseau, voir via internet (dangereux ?).

# Tâches (approximatif)

- Achats/Commandes : 1hj
- Montage Kit Table et mise en route: 2hj
- Impression 3D (pieds+support trans+support cible) : 2hj
- Install config Rpi : 2hj
- Lib de comm Rpi ↔ Table : 2hj
- Lib de comm Rpi ↔ US-SPI : 2hj
- Dev Serveur python pour RPi: 5hj
- Affichage data : 4hj
- Total => environ 20 hj

# Cas d’usage

Le banc pourra être utilisé pour :

- Valider le type de cible (matière, tige, boule, plaque, disque…).
- Caractériser un transducteur de référence (ex Imasonic).
- Caractériser les transducteurs des fournisseurs.
- Valider les échantillons de matière du boîtier, les huiles.
- Mesurer les perturbations introduites pas un miroir acoustique.
- Faire des mesures de calibration pour corriger numériquement les images obtenues.

# Procédure de mesure d’un transducteur

1. Prendre une photo du transducteur sur du papier quadrillé 5x5
2. Noter les références transducteur : Nom constructeur, Nom du produit, Fréquence, Diamètre, Rayon de focalisation, Distance focale, Dimension zone focale à -6dB.
3. Installer en tir direct au raz du support. Faire le zéro au raz et dans l’axe du support.
4. Déplacer cible au point focal en recherchant le maximum d’écho et X. Régler la verticalité de la cible. Régler l’angle horizontal en forçant légèrement sur les tubes du support.
5. Refaire le zéro.
6. Régler le gain à 20dB et la tension à 70V, régler le gain gMax au point justeavant la saturation et augmenter la tension amener la courbe en contact de la ligne 253. Noter le couple (gain, tension)
7. A 160Msps prendre des images (png + json) de l’echo :
  - au point focal, à gMax → 0dB.png/json
  - au point focal 60dB à vide (cible décalée Y -10) → noise_-10mm_60dB.png/json,
  - au point focal 60dB à vide (cible décaléeY -20) → noise_-20mm_60dB.png/json,
  - à -6dB x maxi à gMax → -6dB_x_max.png/json,
  - à -6dB x mini à gMax → -6dB_x_min.png/json,
  - à zero à ?dB (pour le pulse < 255) → pulse.png/json.
8. Retour au contact et Y=0. Refaire le zéro
9. Rechercher le décalage qui affiche l’écho (en général 5-15µs)
10. Lancer une mesure sur 15x250 à 0.2mmx1mm et balayage longitudinal.
11. Sauver l’image (png et json)
12. Compléter fiche de mesure et archiver avec tous les fichiers

# ToDo

- Diagramme de séquence des différents échanges entre les modules
- Liste des paramètres d’un tir, d’un essai (largeur, longueur, pas en X, pas en Y…)
- Types d’essais : un seul tir, exploration à pas fixe, exploration à pas variable, exploration synthétique « intelligente » (recherche de points caractéristiques).
- Définir la procédure de caractérisation d’un transducteur et le livrable associé.

Spécification : echoBench [2017-09-01 SPEC echo_bench_tranducer_test_bench fr] v2 5/5

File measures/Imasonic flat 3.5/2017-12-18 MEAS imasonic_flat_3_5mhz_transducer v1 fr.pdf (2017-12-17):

## Mesures : Transducteur Imasonic Flat 3.5MHz

Caractéristiques du transducteur Imasonic Flat 3.5MHz

Objet : | Résultat du transducteur Imasonic Flat 3.5MHz.
Réf/Fichier : | 2017-12-18 MEAS imasonic_fat___5mhz_transducer v1 fr
Révision : | v1 | 2017-12-17 | BVi | Création
Révision : | En cours ...

TODO

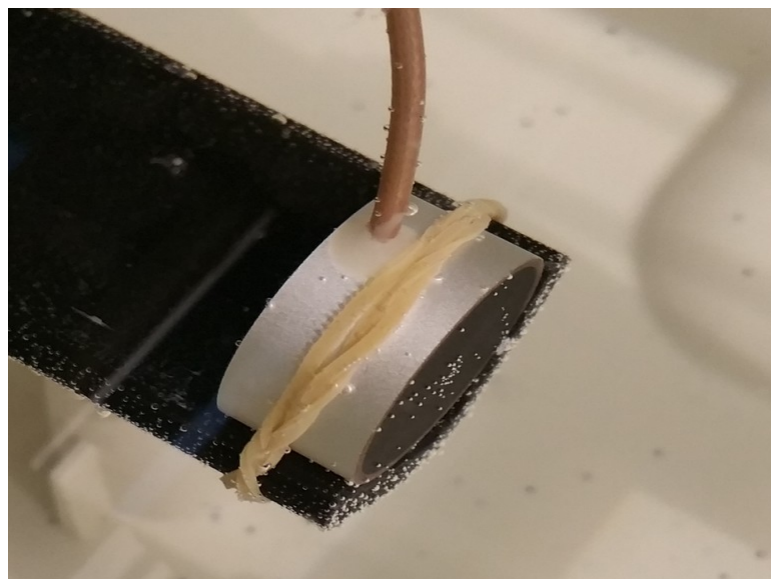
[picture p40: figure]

## Données constructeur

Les références constructeur lisibles sur le transducteur sont :

- TODO

## Mesure du champ

Par déplacement d’un fl nylon de 0.15mm sur une surface de _00mm x 25mm et après réglage du banc pour obtenir un écho mesuré maximum au point focal.

Les mesures sont efectuées avec une tension de 75V et 26dB d’amplifcation.

Mesures : Imasonic fat 3.5MHz v1 2017-112118 MEAS imasonicffatf3f5mhzftransducer v1 frr | 1/4

## Champ d’amplitude

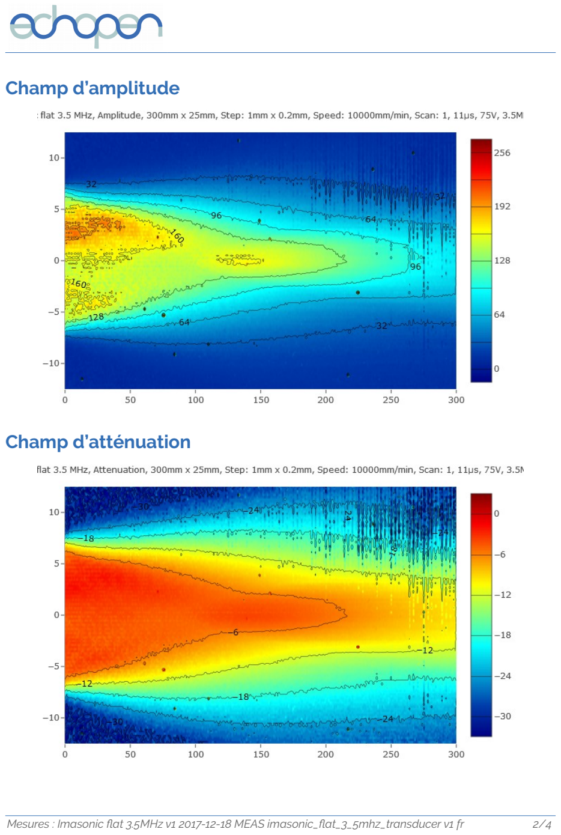
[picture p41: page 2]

## Champ d’atténuation

Mesures : Imasonic fat 3.5MHz v1 2017-112118 MEAS imasonicffatf3f5mhzftransducer v1 frr | 2/4

## Champ de focalisation

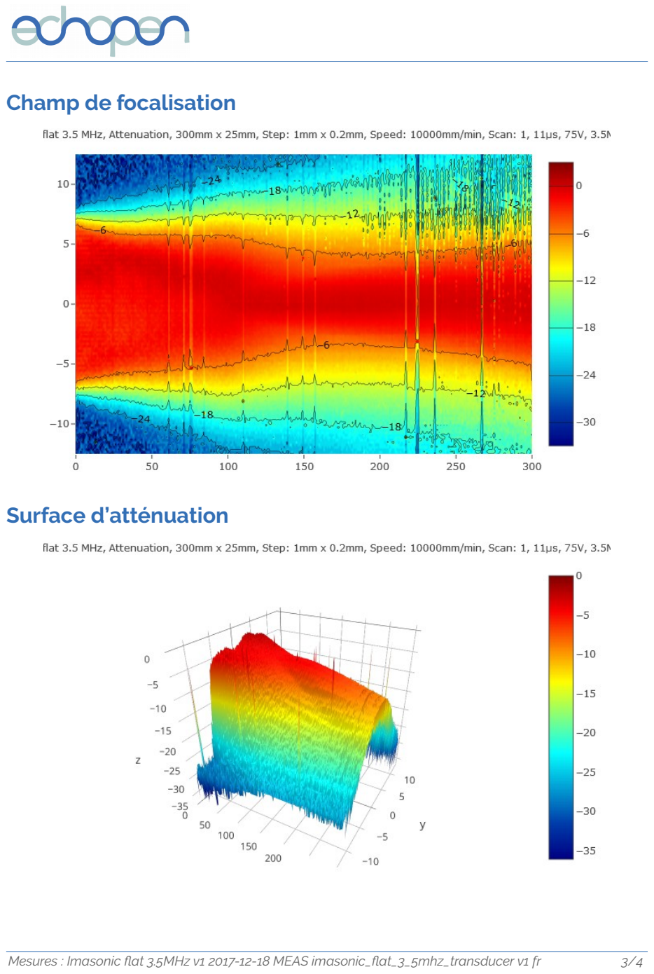
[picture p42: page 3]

## Surface d’atténuation

Mesures : Imasonic fat 3.5MHz v1 2017-112118 MEAS imasonicffatf3f5mhzftransducer v1 frr | 3/4

## Signal d’écho

Signal de l’écho en diférents points caractéristiques.

## Evolution selon axe X

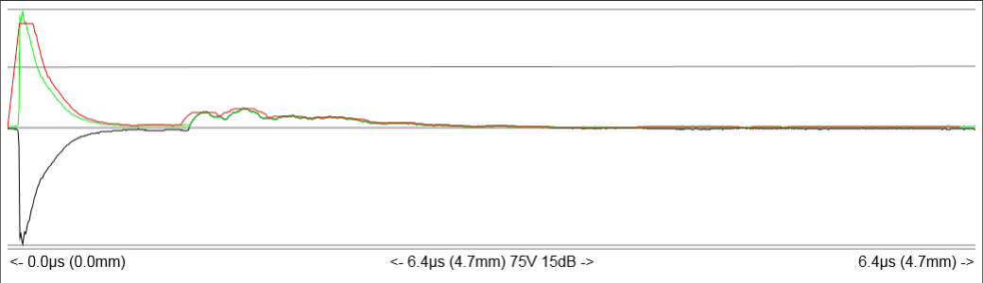
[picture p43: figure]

Forme du pulse mesuré sur le transducteur.

X=120mm

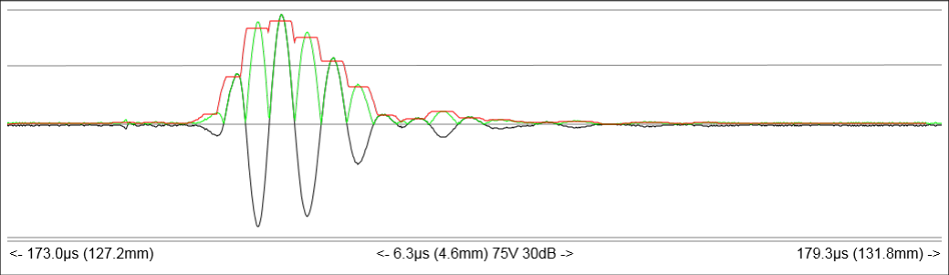
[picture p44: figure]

## Evolution selon axe Y

TODO

Mesures : Imasonic fat 3.5MHz v1 2017-112118 MEAS imasonicffatf3f5mhzftransducer v1 frr | 4/4

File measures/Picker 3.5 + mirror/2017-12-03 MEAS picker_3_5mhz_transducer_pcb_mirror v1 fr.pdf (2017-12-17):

## Mesures : Picker 3.5MHz miroir

Caractéristiques du transducteur de laboratoire Picker 3.5MHz tirant sur un miroir à 45°

Objet : | Résultat du transducteur de laboratoire Picker 3.5MHz avec miroir à 45°.
Réf/Fichier : | 2017-12-03 MEAS picker_3_5mhz_transducer_pcb_mirror v1 fr
Révision : | v1 | 2017-12-03 | BVi | Création
Révision : | En cours

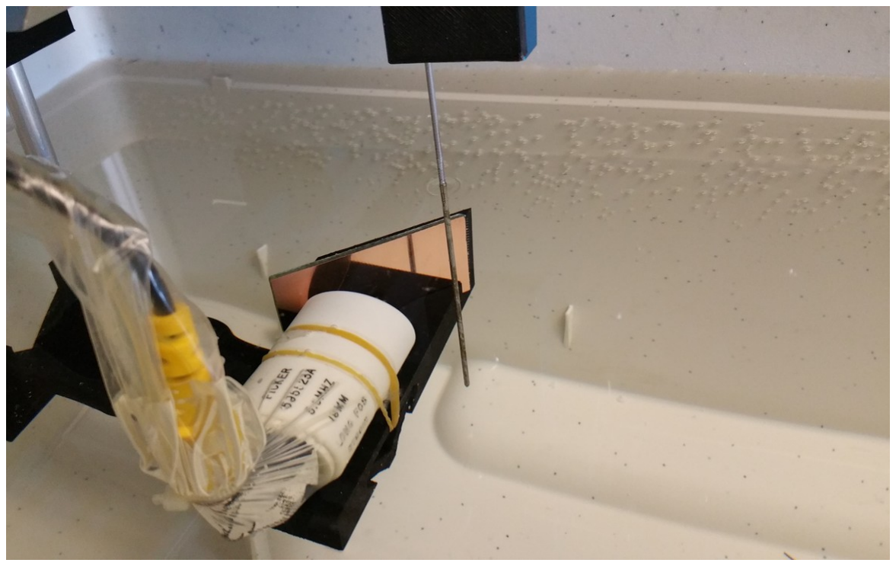
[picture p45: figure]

Le passage de ce transducteur Picker 3.5MHz tirant sur un miroir cuivre de PCB en sur le banc a permis de mesurer une zone focale à -6db de 74mm s’étendant de x=29mm à x=103mm avec un point focal situé à x=51mm. La largeur de la zone focale au point focale est de 2.2mm.

Sachant que la présence du miroir rallonge le chemin acoustique de 45µs soit 33mm.

## Données constructeur

Les références constructeur lisibles sur le transducteur sont :

- PICKER, 565523A, 3.5MHz, 19MM, LONG FOS, 5790IR, SERIES L
- Miroir, cuivre de PCB simple face.

## Mesure du champ

Par déplacement d’un fl nylon de 0.15mm sur une surface de 250mm x 15mm et après réglage du banc pour obtenir un echo mesuré maximum au point focal.

Les mesures sont efectuées par défaut avec une tension de 75V et 17dB d’amplifcation.

Mesures : Picker 3.5MHz miroir v1 2017-12-03 MEAS picker_3_5mhz_transducer_pcb_mirror v1 fr | 1/10

## Champ d’amplitude

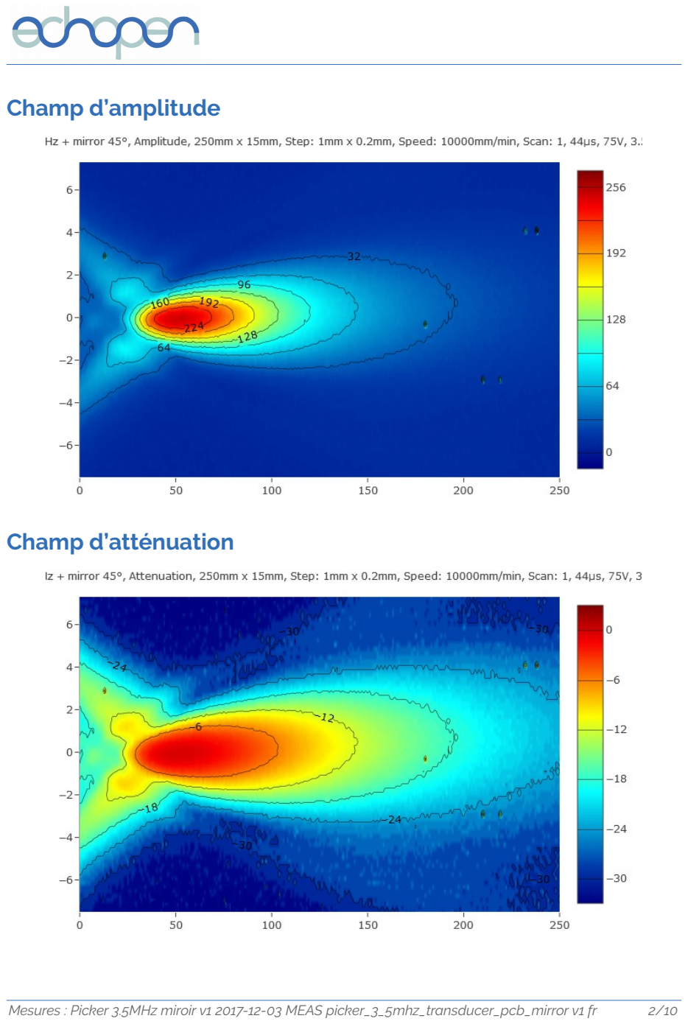
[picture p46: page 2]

## Champ d’atténuation

Mesures : Picker 3.5MHz miroir v1 2017-12-03 MEAS picker_3_5mhz_transducer_pcb_mirror v1 fr | 2/10

## Champ de focalisation

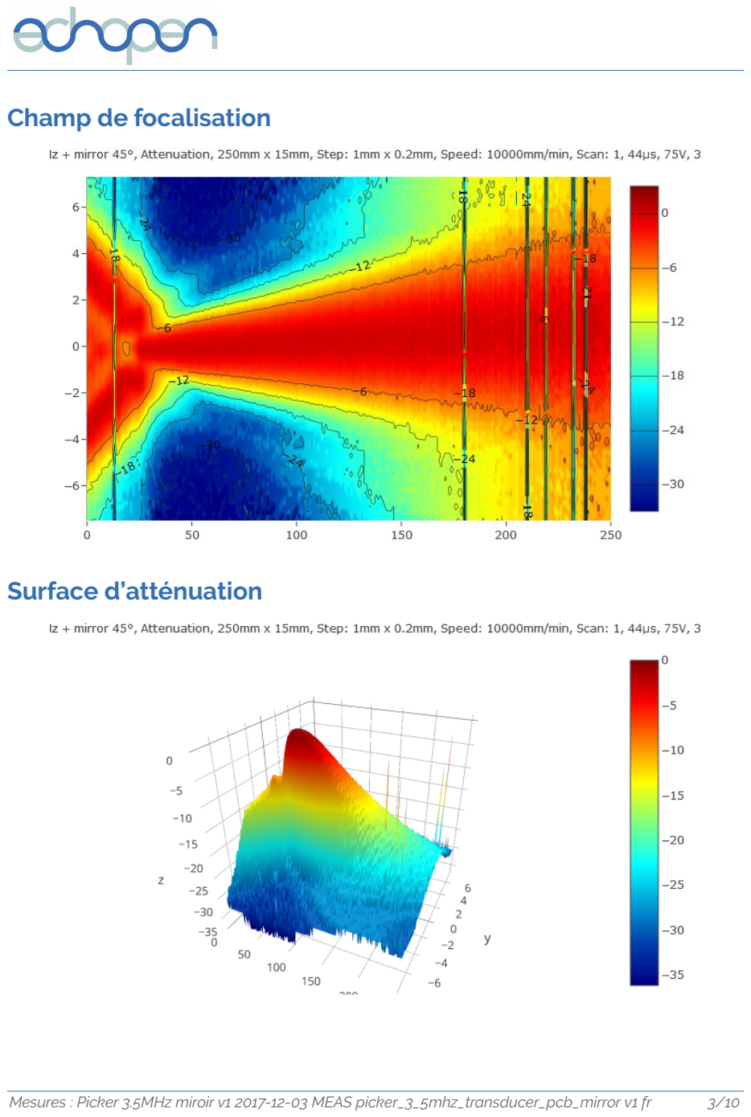
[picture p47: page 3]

## Surface d’atténuation

Mesures : Picker 3.5MHz miroir v1 2017-12-03 MEAS picker_3_5mhz_transducer_pcb_mirror v1 fr | 3/10

## Signal d’écho

## Evolution selon axe X


Signal de l’écho en diférents points caractéristiques.

Forme du pulse mesuré sur le transducteur. Noter l’écrêtage et le nombre de cycles d’oscillation.

Zone de champ proche, amplifcation à 30dB. On constate les perturbations induites par le miroir.

Perturbations derrière la cible à X=40mm (proche point focal) et très fort gain 50dB.

Perturbations derrière la cible à X=200mm et très fort gain 50dB.

Point d’entrée dans la zone focale à -6dB. X=33

Mesures : Picker 3.5MHz miroir v1 2017-12-03 MEAS picker_3_5mhz_transducer_pcb_mirror v1 fr | 4/10


Point d’entrée dans la zone du point focale à 0dB. X=45

Point de sortie dans la zone du point focale à 0dB. X=60

Point de sortie de la zone focale à -6dB. X=109

## Evolution selon axe Y

Autour du point focal.

X=50 Y=1.2

Y=1.0

Mesures : Picker 3.5MHz miroir v1 2017-12-03 MEAS picker_3_5mhz_transducer_pcb_mirror v1 fr | 5/10


Y=0.8

Y=0.6

Y=0.4

Y=0.2

Y=0

Mesures : Picker 3.5MHz miroir v1 2017-12-03 MEAS picker_3_5mhz_transducer_pcb_mirror v1 fr | 6/10


Y=-0.2

Y=-0.4

Y=-0.6

Y=-0.8

Y=-1.0

Mesures : Picker 3.5MHz miroir v1 2017-12-03 MEAS picker_3_5mhz_transducer_pcb_mirror v1 fr | 7/10


Y=-1.2

Y=-10, gain 60dB

Y=-20, gain 60dB

## Signaux à fort gain

X=40 (~= Point focal) gain=50dB

X=200 gain=50dB

Mesures : Picker 3.5MHz miroir v1 2017-12-03 MEAS picker_3_5mhz_transducer_pcb_mirror v1 fr | 8/10

## Miroirs de mauvaise qualité

## Fibre de verre (arrière de PCB)


## PLA (impression 3D, couches 0.2mm)

Mesures : Picker 3.5MHz miroir v1 2017-12-03 MEAS picker_3_5mhz_transducer_pcb_mirror v1 fr | 9/10


Mesures : Picker 3.5MHz miroir v1 2017-12-03 MEAS picker_3_5mhz_transducer_pcb_mirror v1 fr 10/10

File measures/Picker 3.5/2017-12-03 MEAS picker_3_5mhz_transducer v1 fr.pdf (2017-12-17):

## Mesures : Transducteur Picker 3.5MHz

Caractéristiques du transducteur de laboratoire Picker 3.5MHz

Objet : | Résultat du transducteur de laboratoire Picker 3.5MHz.
Réf/Fichier : | 2017-12-03 MEAS picker_3_5mhz_transducer v1 fr
Révision : | v1 | 2017-12-03 | BVi | Création
Révision : | En cours ...


Le passage de ce transducteur Picker 3.5MHz sur le banc a permis de mesurer une zone focale à -6db de 95mm s’étendant de x=49mm à x=144mm avec un point focal situé à x=71mm. La largeur de la zone focale au point focale est de 2.4mm.

## Données constructeur

Les références constructeur lisibles sur le transducteur sont :

- PICKER, 565523A, 3.5MHz, 19MM, LONG FOS, 5790IR, SERIES L

## Mesure du champ

Par déplacement d’un fl nylon de 0.15mm sur une surface de 250mm x 15mm et après réglage du banc pour obtenir un écho mesuré maximum au point focal.

Les mesures sont efectuées avec une tension de 75V et 16dB d’amplifcation.

Mesures : Transducteur Picker 3.5MHz v1 2017-12-03 MEAS picker_3_5mhz_transducer v1 fr | 1/8

## Champ d’amplitude


## Champ d’atténuation

2017-12-03 MEAS picker_3_5mhz_transducer_pcb_mirror v1 fr

## Champ de focalisation


## Surface d’atténuation

## Signal d’écho

Signal de l’écho en diférents points caractéristiques.

## Evolution selon axe X

| Forme du pulse mesuré sur le transducteur. Noter l’écrêtage et le nombre de cycles d’oscillation.


DONNEE MANQUANTE !!! A RAJOUTER sur 102µs | Zone de champ proche, amplifcation à 30dB.


| Point d’entrée dans la zone focale à -6dB. X=50


| Point d’entrée dans la zone du point focale à 0dB. X=69


| Point de sortie dans la zone du point focale à 0dB. X=83

Point de sortie de la
zone focale à -6dB.
X=144

## Evolution selon axe Y

Autour du point focal.


X=70 Y=1.2


Y=1.0


Y=0.8


Y=0.6

Y=0.4


Y=0.2


Y=0


Y=-0.2


Y=-0.4

Y=-0.6


Y=-0.8


Y=-1.0


Y=-1.2


Y=-1.4

Y=-1.6


Y=-10, gain 60dB


Y=-20, gain 60dB

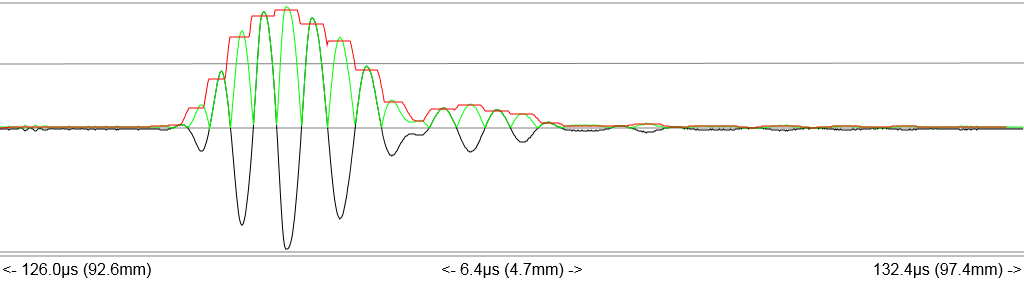
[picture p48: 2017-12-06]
measures/Picker 3.5 + mirror/x60 y0 a0db.png

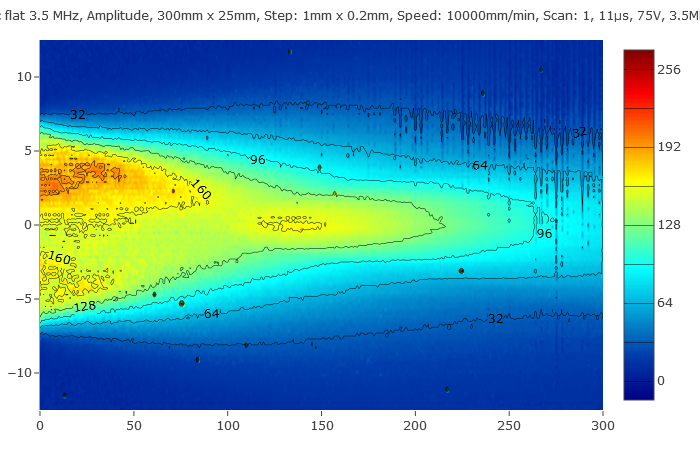
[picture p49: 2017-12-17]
measures/Imasonic flat 3.5/300x25 amplitude_field.png

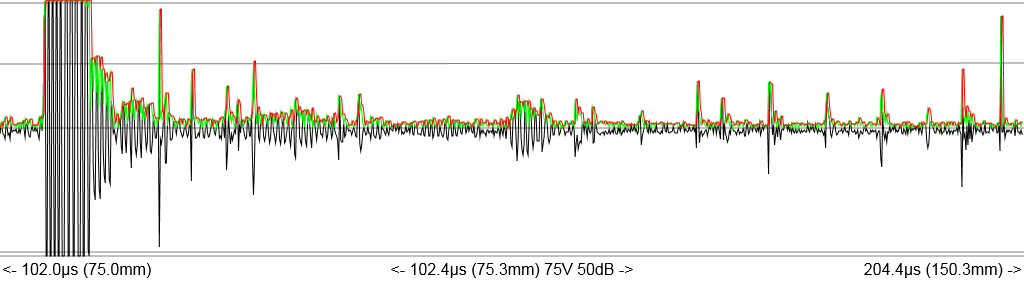
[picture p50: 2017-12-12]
measures/Picker 3.5 + mirror/x40 y0 g50db.png

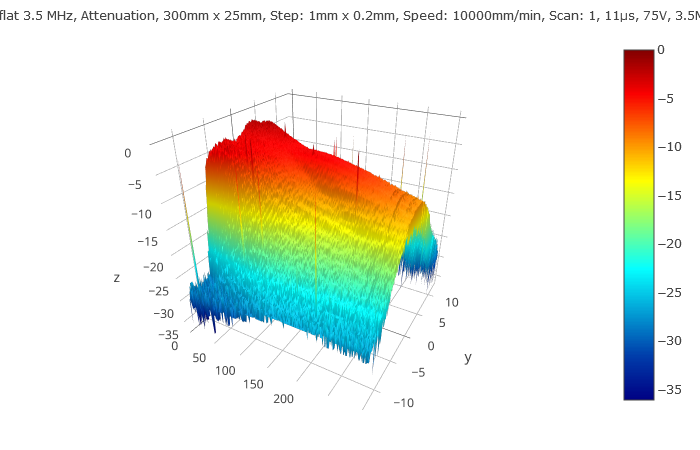
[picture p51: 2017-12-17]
measures/Imasonic flat 3.5/300x25 attenuation_surface.png

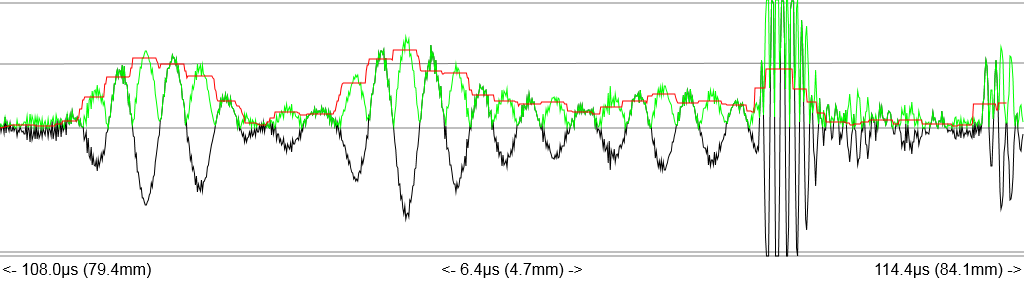
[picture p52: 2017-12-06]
measures/Picker 3.5/x70 y-10 g60db.png

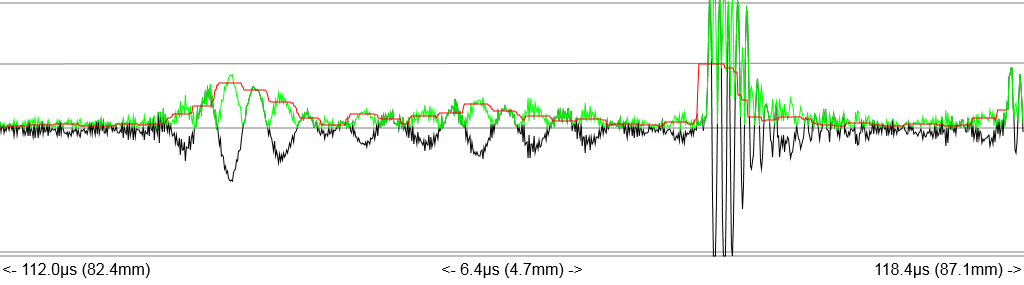
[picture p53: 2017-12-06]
measures/Picker 3.5 + mirror/x50 y-10 g60db.png

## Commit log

2017-12-08 translation FR->EN
    - updated translation of the specifications
    - export PDF current version of specifications
    - translation and update of the root readme
2017-12-08 foot design v3
    [echo_bench_foot_v3_fcv16.FCStd]
2017-12-12 update foot v3
    [echo_bench_foot_v3_fcv16.FCStd]
2017-12-13 Added washer design and small flange for US-SPI
    [echo_bench_pcb_frame_fcv17.FCStd, echo_bench_pcb_frame_flange.stl, echo_bench_pcb_frame_washer.stl]
2017-12-13 feet v3 test and prod
    [echo_bench_foot_v3.stl, echo_bench_foot_v3_fcv16.FCStd]
2017-12-17 Raspberry Pi 0 W burned, use a new one :-(
    Due to a bad connection
